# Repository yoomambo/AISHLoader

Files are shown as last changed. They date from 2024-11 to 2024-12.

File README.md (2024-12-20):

# Installation
First, download the application and install dependencies:
```bash
git clone https://github.com/BenjaminLam9838/AISHLoader
cd AISHLoader
```

Create a virtual environment and install the dependencies.  This app was built on Python 3.9.13 ([pyFirmata has issues in 3.11 [1]](#1-pyfirmata-has-issues-in-311))
```bash
python3.9 -m venv .venv
source .venv/bin/activate
pip install --upgrade pip
pip install -r requirements.txt
```
# To do:
Hardware:
- [ ] Adjust linear rail alignment. Currently, it is slightly misaligned with the alignment rails and does not insert perfectly
- [ ] Increase stiffness of the gripper if the gripping is not consistent.

Software:
- [ ] Test abortion feature.  Currently, the abortion procedure is not quite complete
- [ ] Known bug: pausing the queue when an experiment is running will make the queue pause after the current experiment is done (will not send the next experiment after finish).  But pressing resume before the experiment is done just sends the next experiment, even if the current one is not finished, causing an error. Likely fix: change logic to just toggle the queue pause state, and remove sendNextItem() function in the resume button callback.
- [ ] Test data saving location for XRD data

# Control Interface Guide


The web UI is broken into 4 main parts:
- Add to queue (Blue) - adds items to the queue with all the experimental parameters.
- Queue (Green) - displays queued items and updates when items are executed. The items can be dragged to reorder.
- System status (Red) - displays the current system state.
- Manual control (Orange) - collapsable menu that contains buttons to manually control all components of the AISH Loader.

# System Diagram
## Top-level Flowchart

The python/Flask server controls the entire system. It recieves HTTP requests to the API endpoints either from the website (user input), or from ALab; these HTTP requests are intended to work for both cases and be the minimum set of instructions needed to control the system.

The Flask server then communicates over pyFirmata (based on serial) with the Arduino to control the gripper and linear rail, and directly communicates with the Ender3 over serial.  This server runs on the XRD computer and writes to a local directory to control the XRD.

## Wiring Diagram:


# CAD
A Solidworks CAD is supplied in the /cad.  A full BOM is left in /documentation.

# Stepper Motor Driver
A `STEPPERONLINE Stepper Motor Driver` controller was used to control the linear rail. It was set to 400 pulses/rotation, meaning that each time the Arduino pulses the motor driver, the motor rotates 1/400 of a rotation.  The pinout used is shown below:



Errors
===
### Manual adjustment of Ender3
Sometimes, manual adjustment of the Ender3 needs to be done to put it in a position that is good for testing.  The gantry cannot be manipulated when the Ender is powered, so it must be de-powered.  Remember to unplug the Serial connection, then power down the Ender.  Follow the procedure in [Ender3 Connection](#Ender3-Connection).

### Ender3 Connection
When the Ender3 is not connected properly, the unit scale gets changed.  This usually results in the Ender moving about 1/2 the distance that is inputted.  To fix, restart the system, unplug the serial connection to the Ender, and power cycle the Ender.  Make sure to wait for the Ender to start up and be ready, then plug in the serial connection and try the connection.

### Connecting Serial
The system has trouble connecting at first.  Unplug the serial connections, then unpower/repower the extender cables, then reconnect the serial connections.  Basically have to power/unpower the first connector, then connect the next connector, unpower and power that, then can continue connecting.

Notes
===
#### [1] pyFirmata has issues in 3.11
[pyFirmata's Github](https://github.com/tino/pyFirmata/tree/master) says it runs on python 3.7.

When calling ```board = pyfirmata.Arduino('/dev/tty.usbmodem21101')```, an AttributeError is thrown: ```AttributeError: module 'inspect' has no attribute 'getargspec'. Did you mean: 'getargs'?```.
ChatGPT says:
> The error you're encountering is due to the use of the inspect.getargspec method in pyfirmata, which has been deprecated and removed in Python 3.11. Instead, inspect.getfullargspec should be used.

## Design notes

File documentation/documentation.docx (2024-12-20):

# Hardware

## app.py

Sets up the Flask server by defining all the endpoints. The endpoints are organized into API Endpoints, which are the endpoints intended for use, and manual endpoints, which give direct manual control over the available system actions.

On start, the application attempts a connection to the 3D printer over serial and performs its homing procedure. It then attempts a connection to the Arduino over serial/pyFirmata and homes its components. If either of these connections fail, the server will not start, unless WEBSITE_TEST_MODE is on.

The connections to the Ender and Arduino are made by a AISHLoader object, which contains all the relevant functions and actions for the loading/unloading procedures. A AISHExperiment object is created when the system is given an experiment and this class contains all the relevant functions and actions to execute an XRD experiment. The aish_experiment variable is set to null if there is no currently running experiment.

## AISHExperiment.py

Contains the relevant functions and actions to execute an XRD experiment. The Diffractometer class is taken from Nathan’s AdaptiveXRD code (https://github.com/njszym/AdaptiveXRD) to run the Bruker. The run_sequence function is a blocking function that runs all XRD scans at the given temperatures. Since it is blocking, the Flask server runs this function in a separate thread to prevent the server from stalling when an experiment runs.

## AISHLoader.py

Contains relevant functions and actions for the loading/unloading procedures. This is meant to be an abstraction layer to help group the low level procedures together.

## ArduinoHardware.py

Contains the control code for the Gripper and Linear rail, which are each subclasses. Each command is assigned a unique Firmata sysex command ID, which instructs the Arduino to execute its various actions. It then listens for an acknowledgement from the Arduino that the command was completed (blocking).

## Ender3.py

Contains the control code for the Ender3. This class writes gcode commands to the serial bus to control movement. Most of the movements utilize _move_to(x,y,z, speed) which is a function that sends the required gcode to move to the specified x,y,z position. This function is also blocking, so each move will be completed before moving to the next.

## AISH_utils.py

Contains classes to handle communication timeouts that may occur. Since the system runs in semi open-loop, some actions are not verified completed. So these functions allow the system to ask the user to confirm that an action was completed.

## StateTracker.py

Helper class that logs the last 100 states. The other hardware classes inherit from this class, so all of them have a list of the last 100 states they were in. These states are just strings. Meant for debugging but could be helpful for logs.

# Website

## templates > index.html

Contains the html for the web UI to queue experiments. Also includes the UI for manual control of all system components

## static > js > app.js

app.js contains all the js components for website communication with the Flask server, and updating components on the webpage.

The webpage first loads utils.js, then loads app.js. app.js attaches all button callbacks when the website has loaded. A loop is started to refresh the webpage state every set interval where the webpage asks the Flask server for the current system state and displays that to the webpage.

## static > js > utils.js

utils.js includes tools for rendering the webpage like experiment time estimation, dynamic button layout (the buttons for the sample positions are generated with js).

# Arduino Code

## AISHLoader

Essentially a switch-case list of the different commands that the Arduino will perform.

## Tests > LinearRail_Testing

Tests the Linear rail motion. Takes input from the serial monitor for how many steps to move (+ for up, - for down) and “home” to execute the homing procedure. Use this to dial in the amount of throw for the linear rail.

## Tests > Servo_SerialTesting

Tests the gripper servo motion. Takes input from the serial monitor of the angle to move the servo to.

# Calibration

The sample positions of the Ender sometimes has to be recalibrated. The positions are found by finding the 4 corner positions, and the rest are interpolated. The calibration script moves the gripper to the desired position, moves down to grab the sample, lifts it, then puts it back. The sample should not scrape against the holder. My testing seems to show that there +/- 0.3 mm of tolerance from perfectly centered.

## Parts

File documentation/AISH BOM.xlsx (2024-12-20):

Assembly | Part | Quantity | Link | Comments | Price
InSituXRD_ASSM > StageLoader_ASSM | FuyuRail_ASSM | 1 | https://www.amazon.com/FUYU-Actuator-Motorized-Stepper-Sliders/dp/B0CRKGDDY6?ref_=ast_sto_dp&th=1 |  | 84.15
InSituXRD_ASSM > StageLoader_ASSM > RailFrame_ASSM | 47065T411 | 2 | https://www.mcmaster.com/47065T101-47065T553/ | T-Slotted Framing 12" | 8.67
InSituXRD_ASSM > StageLoader_ASSM > RailFrame_ASSM | 47065T553 | 3 | https://www.mcmaster.com/47065T101-47065T553/ | T-Slotted Framing 6" | 6.06
InSituXRD_ASSM > StageLoader_ASSM > RailFrame_ASSM | 47065T239 | 2 | https://www.mcmaster.com/47065T239/ |  | 8
InSituXRD_ASSM > StageLoader_ASSM > RailFrame_ASSM | 47065T663_Silver Gusset Bracket | 5 | https://www.mcmaster.com/47065T663/ |  | 9.97
InSituXRD_ASSM > StageLoader_ASSM > StageMount_Multipart_ASSM | 5537T658_T-Slotted Framing | 2 | https://www.mcmaster.com/5537T658/ | Stage mount bracket | 10.54
InSituXRD_ASSM > StageLoader_ASSM > StageMount_Multipart_ASSM | StageMount_Multipart_ MountPlate | 1 |  | 3D print
InSituXRD_ASSM > StageLoader_ASSM > StageMount_Multipart_ASSM | StageMount_Multipart_ TopPlate | 1 |  | 3D print NYLON
InSituXRD_ASSM | 91290A332 | 4 | https://www.mcmaster.com/91290A332/ | Bolts for Stage | 0.222
InSituXRD_ASSM | 9657K275 | 4 | https://www.mcmaster.com/9657K275/ | Springs for stage | 0.965
InSituXRD_ASSM > SampleLoader_ASSM | 01 MAIN ASM Ender_3 | 1
InSituXRD_ASSM > SampleLoader_ASSM | SampleLoader_SampleBufferPlate | 1 |  | 3D print
InSituXRD_ASSM > SampleLoader_ASSM > Gripper_ASSM | DS3218MG MS24 Digital Servo 270 | 1
InSituXRD_ASSM > SampleLoader_ASSM > Gripper_ASSM | Gripper_ServoCouplin g | 1 |  | 3D print
InSituXRD_ASSM > SampleLoader_ASSM > Gripper_ASSM | Gripper_ServoMount_V 2 | 1 |  | 3D print
InSituXRD_ASSM > SampleLoader_ASSM > Gripper_ASSM | Gripper_Claw_OffsetL_ v2 | 1 |  | 3D print
InSituXRD_ASSM > SampleLoader_ASSM > Gripper_ASSM | Gripper_Claw_OffsetR_ v2 | 1 |  | 3D print
InSituXRD_ASSM > SampleLoader_ASSM > Gripper_ASSM | 91290A117 | 2 | https://www.mcmaster.com/91290A117/ | bolts for gripper arms | 0.1129

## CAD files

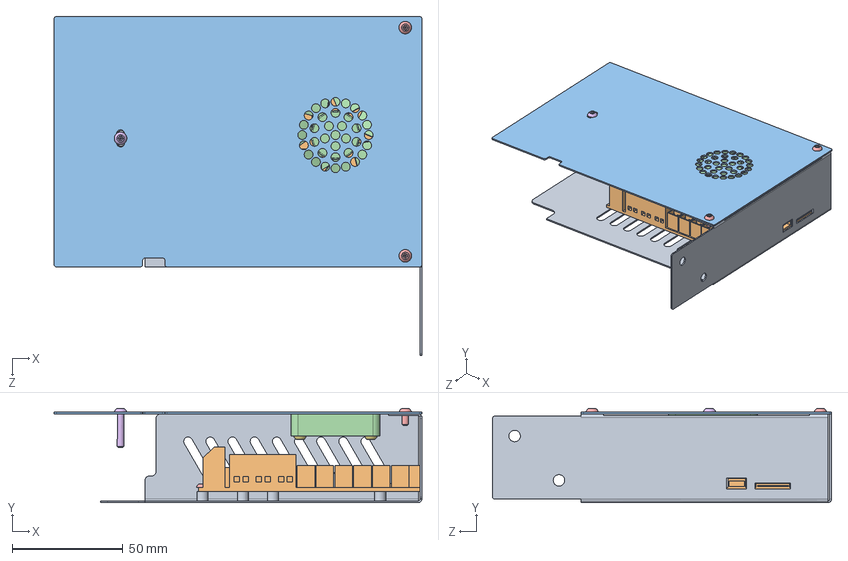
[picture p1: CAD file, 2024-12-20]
cad/SampleLoader/Ender-3/ASM Electronic Enclosure.SLDASM
166.0 x 42.5 x 153.0 mm
Sheetmetal enclosure bottom
Control panel
Sheetmetal enclosure top
Case fan
M3X6Pan Head Screw x 6
M3X16 Pan Head Screw
M3X10 Pan Head Screw x 2

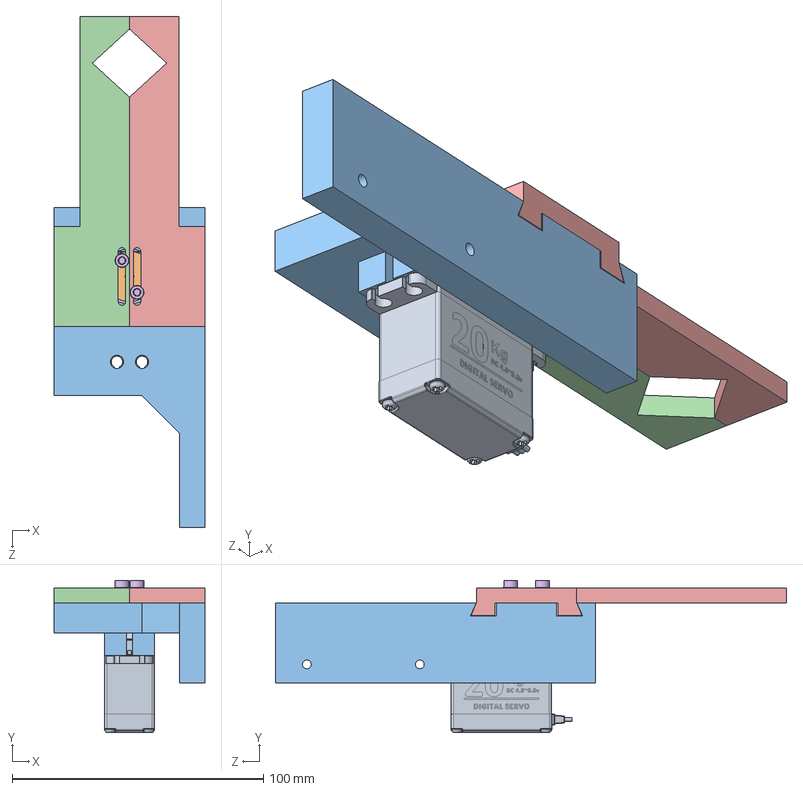
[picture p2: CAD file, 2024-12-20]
cad/SampleLoader/Gripper/Gripper_ASSM_v2.SLDASM
60.0 x 60.7 x 203.6 mm
DS3218MG MS24 Digital Servo 270
Gripper_ServoCoupling
Gripper_ServoMount_V2
Gripper_Claw_OffsetL_v2
Gripper_Claw_OffsetR_v2
91290A117_Alloy Steel Socket Head Screw x 2

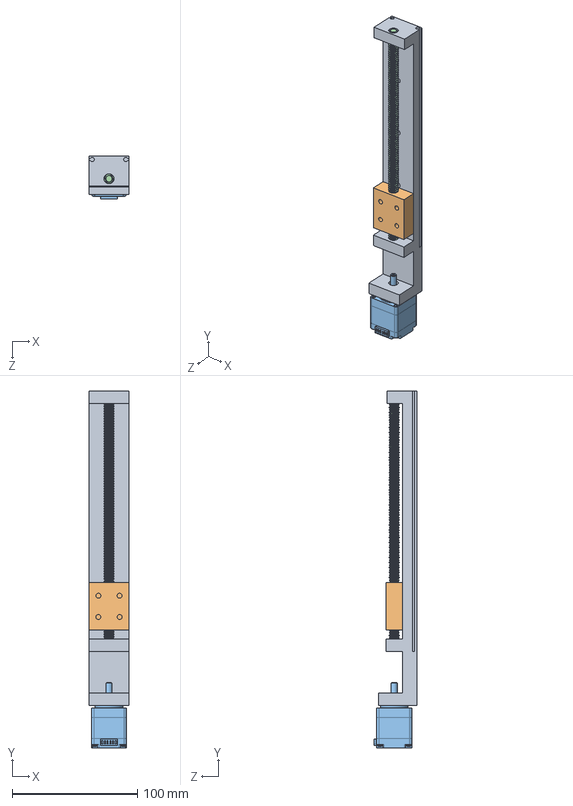
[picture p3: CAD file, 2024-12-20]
cad/StageLoader/FuyuRail/FuyuRail_ASSM.SLDASM
32.0 x 285.0 x 34.0 mm
FuyuRail_Body
FuyuRail_Coupling
6627T37_Stepper Motor
97783A170_Fast-Travel Ultra-Precision Lead Screw

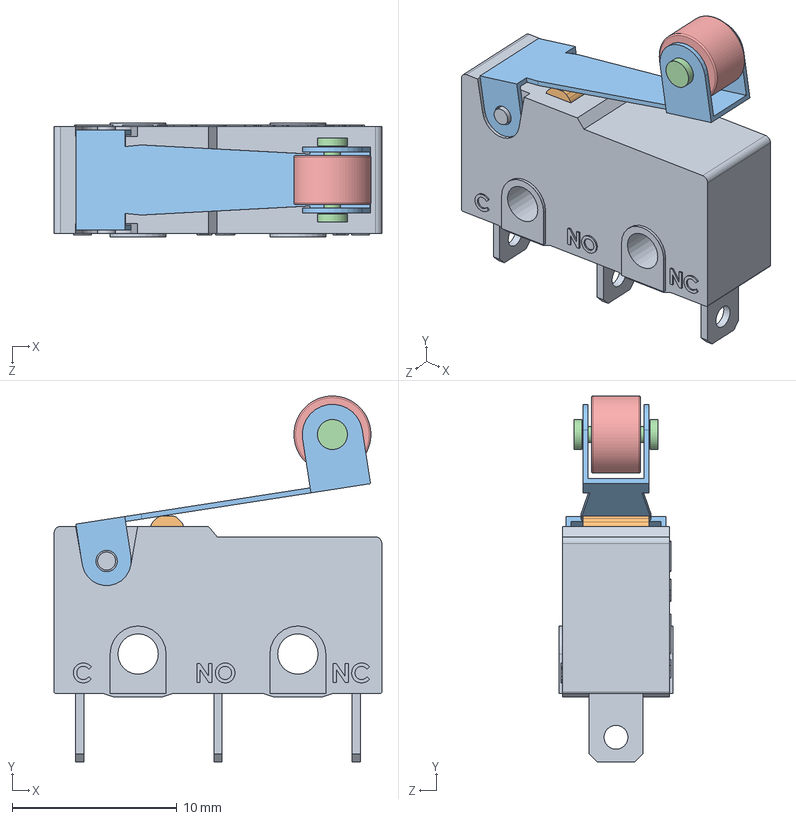
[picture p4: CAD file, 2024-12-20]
cad/StageLoader/limit-switch-19.snapshot.1/Limit Switch.SLDASM
19.9 x 22.2 x 6.90 mm
Switch_Button
Link
Wheel shaft
Wheel

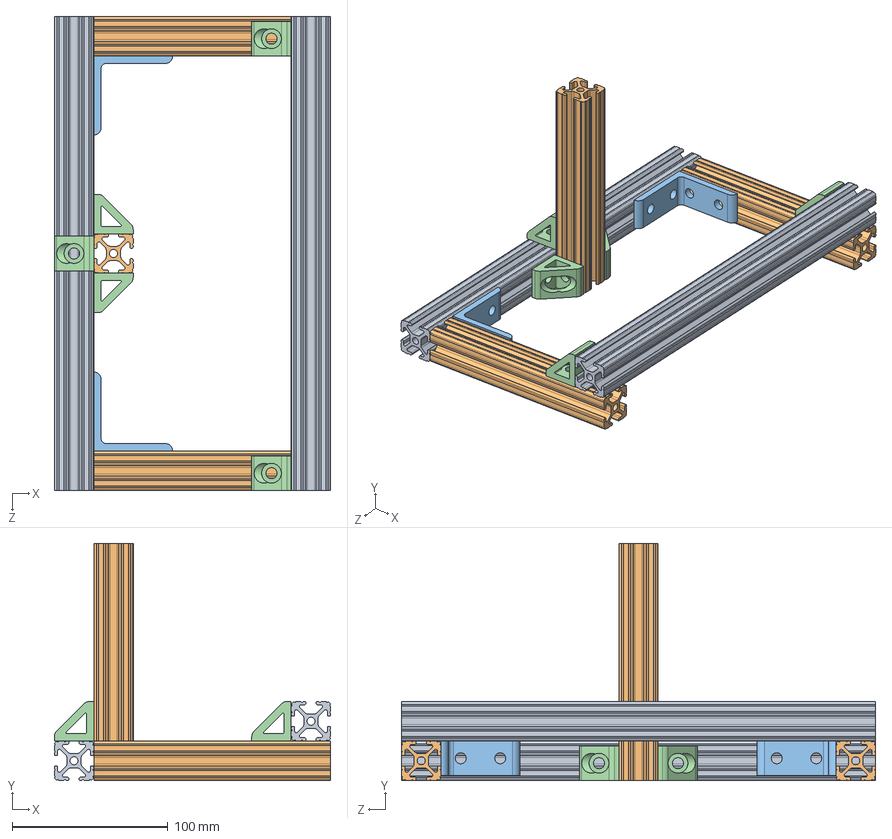
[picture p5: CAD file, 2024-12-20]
cad/StageLoader/RailFrame/RailFrame_ASSM.SLDASM
177.8 x 152.4 x 304.8 mm
47065T411_T-Slotted Framing x 2
47065T553_T-Slotted Framing x 3
47065T239_Silver Corner Bracket x 2
47065T663_Silver Gusset Bracket x 5

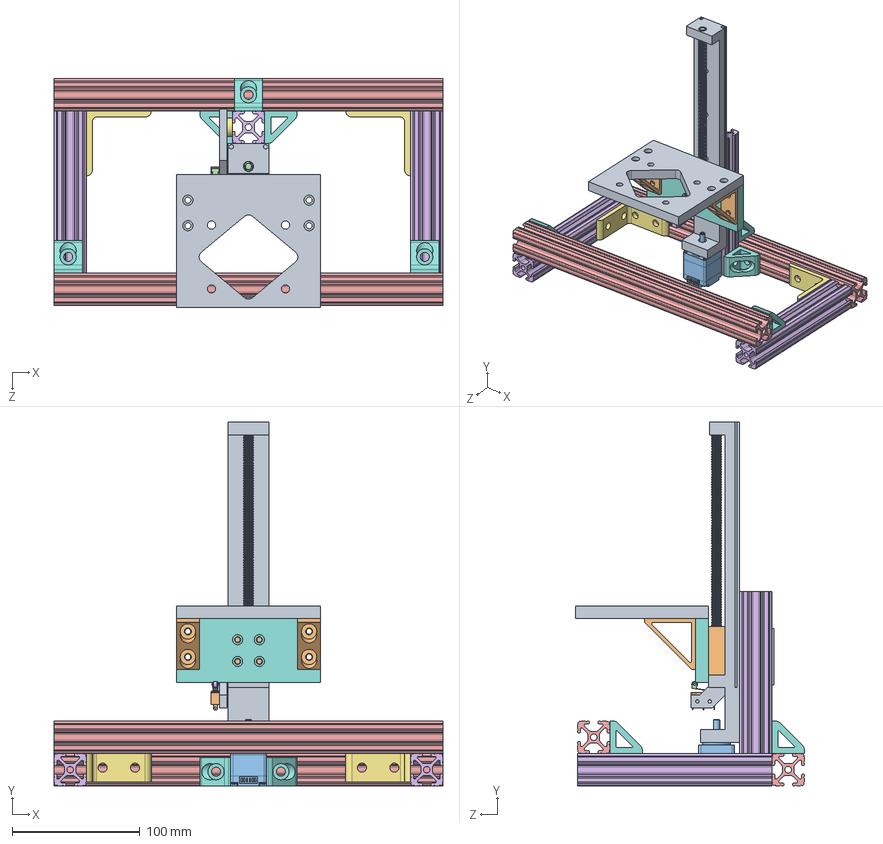
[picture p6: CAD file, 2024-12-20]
cad/StageLoader/StageLoader_ASSM.SLDASM
304.8 x 285.0 x 179.3 mm
FuyuRail_Body
FuyuRail_Coupling
6627T37_Stepper Motor
97783A170_Fast-Travel Ultra-Precision Lead Screw
47065T411_T-Slotted Framing x 2
47065T553_T-Slotted Framing x 3
47065T239_Silver Corner Bracket x 2
47065T663_Silver Gusset Bracket x 5
StageLoader_LimitSwitchTslot2
Switch_Button
Link
Wheel shaft
Wheel
StageLoader_LimitSwitchTslot2_spacer
StageMount_Multipart_MountPlate
StageMount_Multipart_TopPlate
5537T658_T-Slotted Framing x 2

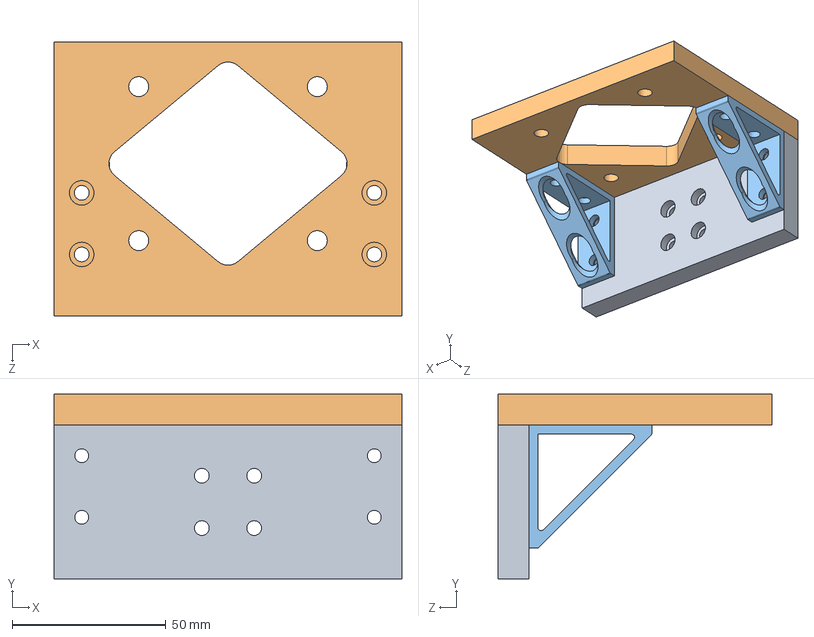
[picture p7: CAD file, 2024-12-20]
cad/StageLoader/StageMount_Multipart/StageMount_Multipart_ASSM.SLDASM
113.0 x 60.0 x 89.0 mm
StageMount_Multipart_MountPlate
StageMount_Multipart_TopPlate
5537T658_T-Slotted Framing x 2

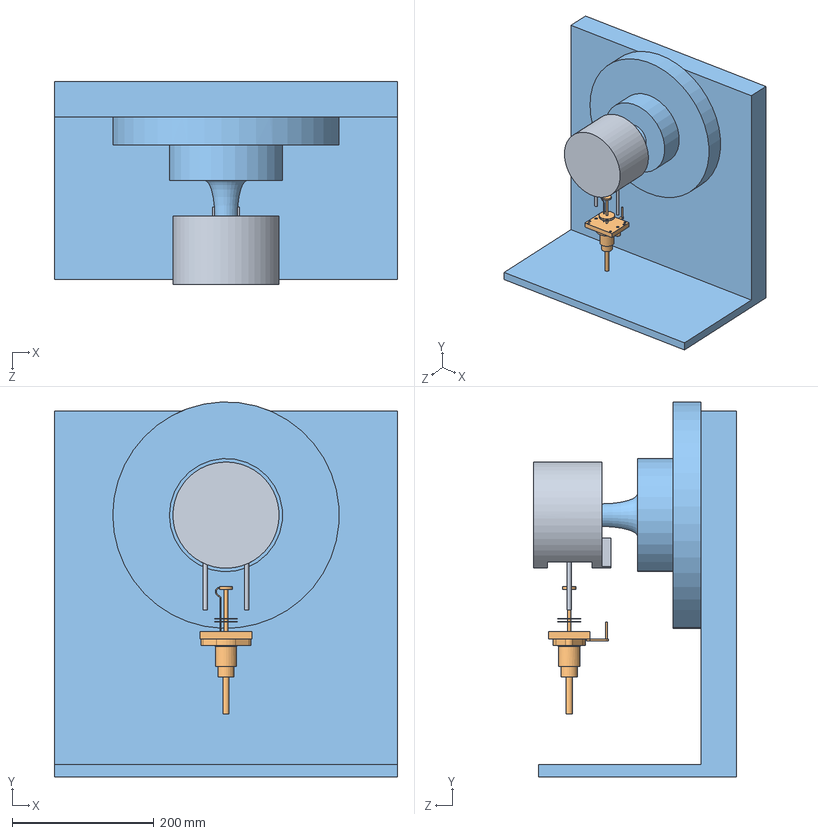
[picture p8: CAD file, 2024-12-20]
cad/XRD/XRD_ASSM.SLDASM
485.0 x 530.0 x 287.0 mm
XRD_FurnaceBody
XRD_SampleStage
XRD_Frame

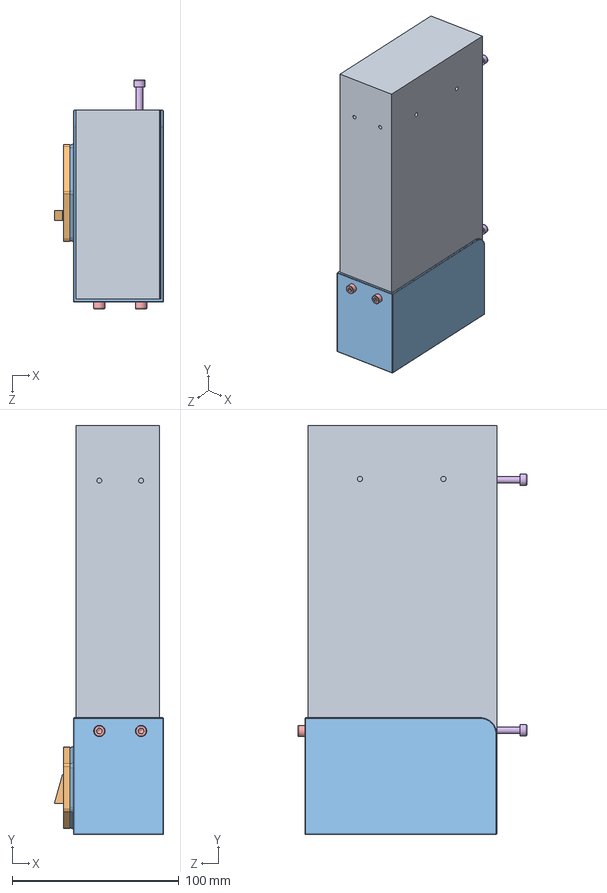
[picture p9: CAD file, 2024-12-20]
cad/SampleLoader/Ender-3/ASM Power Supply.SLDASM
65.5 x 245.0 x 137.0 mm
24V15A power supply
power switch
Power holder
M3X10 Flush Head Screw x 2
M4X8 Socket Head Screw x 2
M4X20 Socket Head Screw x 2

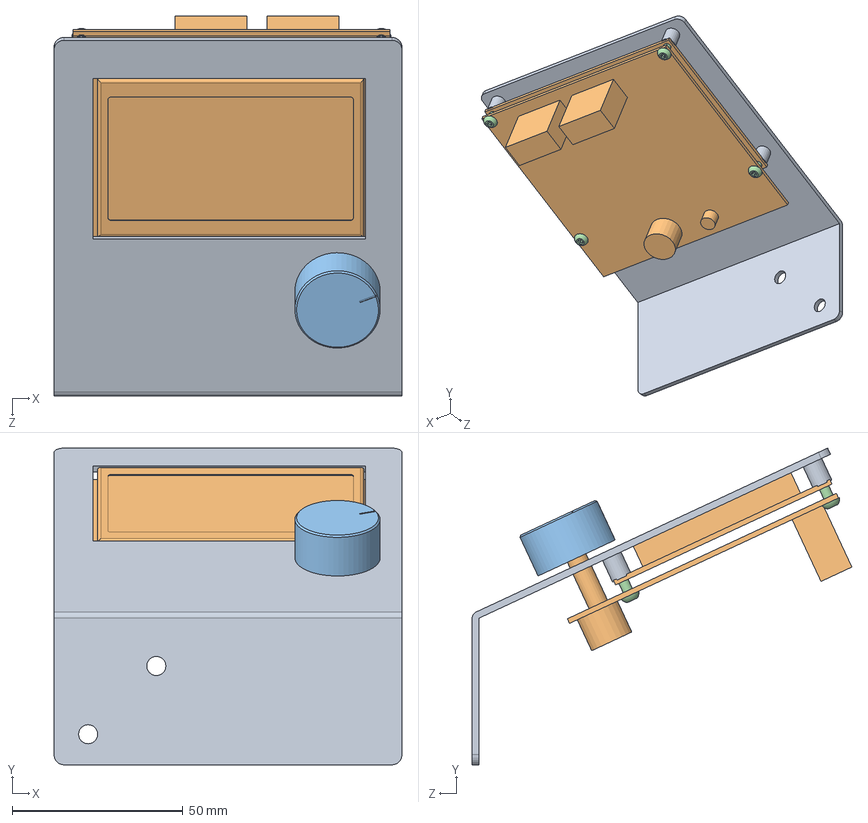
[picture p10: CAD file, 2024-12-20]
cad/SampleLoader/Ender-3/ASM Display.SLDASM
102.0 x 92.9 x 111.3 mm
LCD support
lcd
lcd Knob
M3X8 Pan Head Screw x 4

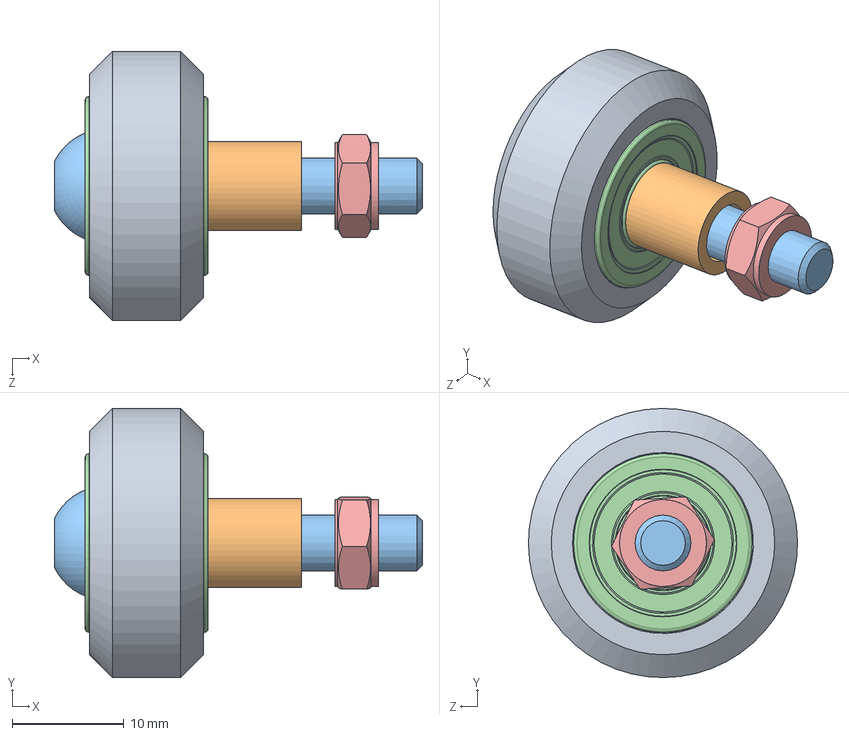
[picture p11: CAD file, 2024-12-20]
cad/SampleLoader/Ender-3/ASM Roller Z-Axis Right.SLDASM
33.0 x 24.1 x 24.1 mm
Rollers
Spacers for rollers
M5X30 Pan Head Screw
625pillow x 2
M5 Self-locking nut

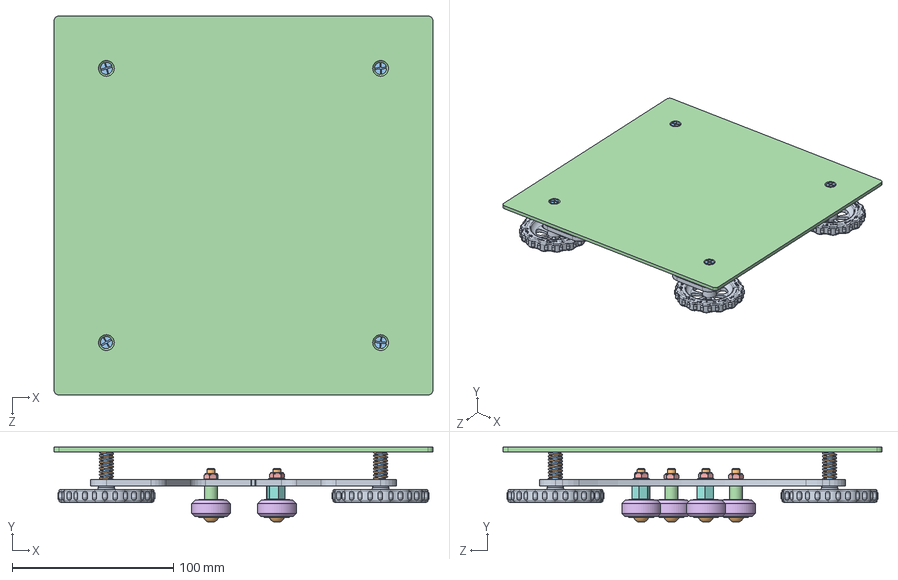
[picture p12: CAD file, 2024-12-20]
cad/SampleLoader/Ender-3/ASM Bed.SLDASM
235.0 x 46.2 x 235.0 mm
Y plate
M5X30 Pan Head Screw x 4
625pillow x 8
Spacers for rollers x 2
M5 Self-locking nut x 4
Rollers x 4
M5 washer x 2
Eccentric column x 2
Hand Twisted Nut x 4
Bed level springs x 4
M4X30 Flush Head Screw x 4
Hot bed

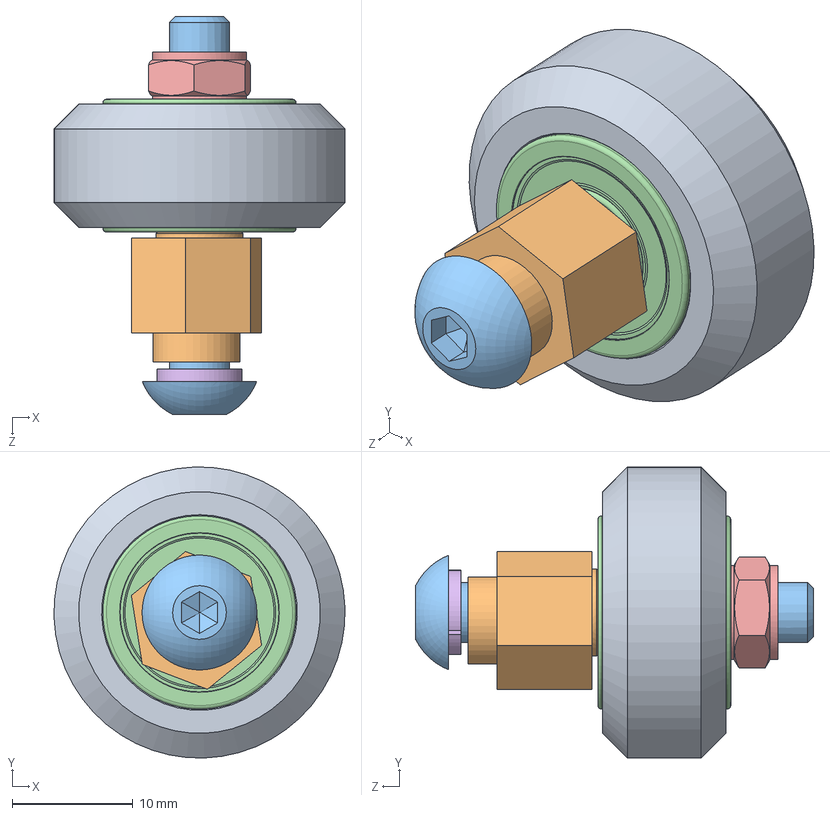
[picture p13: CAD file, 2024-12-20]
cad/SampleLoader/Ender-3/ASM Eccentrical Roller Z-Axis Right.SLDASM
24.1 x 24.1 x 33.0 mm
Rollers
Eccentric column
M5X30 Pan Head Screw
625pillow x 2
M5 Self-locking nut
M5 Split Washer

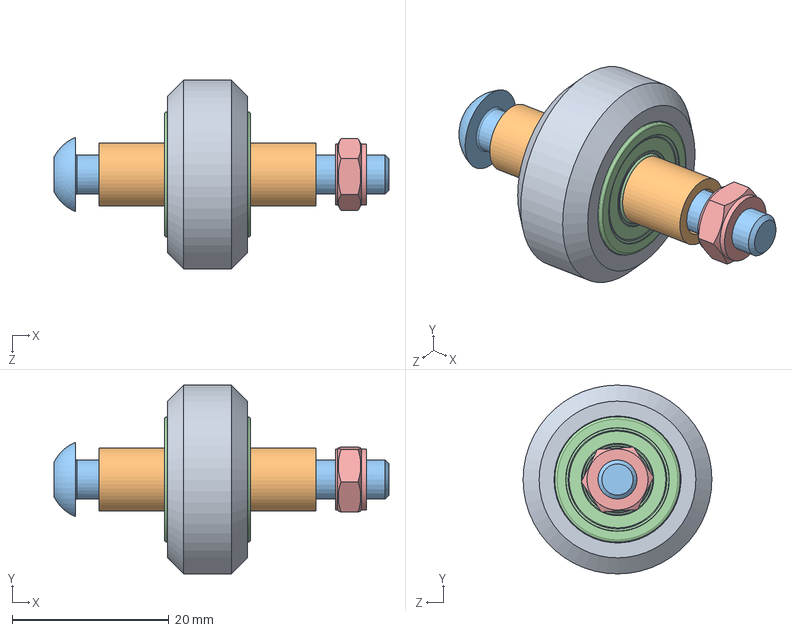
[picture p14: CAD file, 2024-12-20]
cad/SampleLoader/Ender-3/ASM Roller Z-Axis Left.SLDASM
42.8 x 24.1 x 24.1 mm
Rollers
Spacers for rollers x 2
M5X40 Pan Head Screw
625pillow x 2
M5 Self-locking nut

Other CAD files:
cad/SampleLoader/Ender-3/ASM Roller Y-Axis.SLDASM
cad/SampleLoader/Ender-3/ASM Y-Belt Tensioner.SLDASM
cad/SampleLoader/Ender-3/ASM Eccentrical Roller Z-Axis Left.SLDASM
cad/SampleLoader/Ender-3/ASM X-Belt Tensioner.SLDASM
cad/1272T361_Multipurpose 304 Stainless Steel Rod.SLDPRT
cad/91290A332_Alloy Steel Socket Head Screw.SLDPRT
cad/9657K275_Compression Spring.SLDPRT
cad/InsituXRD_AlignmentBracket.SLDPRT
cad/InsituXRD_ControlBox.SLDPRT
cad/InsituXRD_RodHolder.SLDPRT
cad/SampleLoader/Ender-3/2020 Endcap.SLDPRT
cad/SampleLoader/Ender-3/2020 profile.SLDPRT
cad/SampleLoader/Ender-3/2020-2 profile.SLDPRT
cad/SampleLoader/Ender-3/2040-2 profile.SLDPRT
cad/SampleLoader/Ender-3/2040-3L profile.SLDPRT
cad/SampleLoader/Ender-3/2040-3R profile.SLDPRT
cad/SampleLoader/Ender-3/24V15A power supply.SLDPRT
cad/SampleLoader/Ender-3/2GT-pulley.SLDPRT
cad/SampleLoader/Ender-3/4040 profile.SLDPRT
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

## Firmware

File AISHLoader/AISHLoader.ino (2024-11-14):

#include <Boards.h>
#include <Firmata.h>
#include <FirmataConstants.h>
#include <FirmataDefines.h>
#include <FirmataMarshaller.h>
#include <FirmataParser.h>

#include <Servo.h>

Servo gripperServo;  // create Servo object to control a servo
#define SERVO_SPEED_DELAY 15
#define servoPin 9


// Define stepper motor connection pins
#define RAIL_limPin 5   //Limit switch
#define RAIL_dirPin 6   // Direction pin
#define RAIL_stepPin 7  // Step pin
#define RAIL_enPin 8    //Enable pin

// Define the number of steps per revolution for motor
#define RAIL_STEPS_PER_REV 400
#define RAIL_PULSEWIDTH 300  // Controls the speed, longer = slower
int RAIL_stepCount = -1;     // Tracks the current number of steps of the stepper motor rail.  75*400 = 30 000, which is storable in signed int

void setup() {
  Firmata.setFirmwareVersion(FIRMATA_FIRMWARE_MAJOR_VERSION, FIRMATA_FIRMWARE_MINOR_VERSION);
  Firmata.begin(57600);

  // Attach SysEx callback handler
  for (uint8_t i = 0; i < 0x50; i++)
    Firmata.attach(i, sysexCallback);

  //Initialize servo to 0 (open)
  gripperServo.attach(servoPin);  // attaches the servo to the Servo object
  moveServo(0);

  //Initialize the input/output pins for the linear rail
  pinMode(RAIL_stepPin, OUTPUT);
  pinMode(RAIL_dirPin, OUTPUT);
  pinMode(RAIL_enPin, OUTPUT);
  pinMode(RAIL_limPin, INPUT_PULLUP);  //Normally open

  digitalWrite(RAIL_enPin, LOW);    //Turn off current through the motor
  digitalWrite(RAIL_stepPin, LOW);  //Initialize the pulsing pin to low
  digitalWrite(RAIL_dirPin, HIGH);  //Set direction to up
}

void loop() {
  // Handle any incoming Firmata messages
  while (Firmata.available()) {
    Firmata.processInput();
  }
}

void sysexCallback(byte command, byte argc, byte* argv) {
  // Echo back the received SysEx message
  switch (command) {
    //LINEAR RAIL CALLBACKS
    case 0x20:  //Linear rail go up
      {
        rotateMotor(10 * RAIL_STEPS_PER_REV);
        byte data = 0xFF;
        Firmata.sendSysex(command, 1, &data);  //Send a 0xFF byte to indicate it is finished and successful
        break;
      }
    case 0x21:  //Linear rail go down
      {
        rotateMotor(-10 * RAIL_STEPS_PER_REV);
        byte data = 0xFF;
        Firmata.sendSysex(command, 1, &data);  //Send a 0xFF byte to indicate it is finished and successful
        break;
      }
    case 0x22:  //Get the stepper motor count of the linear rail
      {
        byte data[2];

        // Break the int into 2 bytes
        data[0] = (RAIL_stepCount >> 8) & 0xFF;
        data[1] = RAIL_stepCount & 0xFF;

        // Send the data as a Sysex message
        Firmata.sendSysex(command, 2, data);  // 0x71 is an example command ID
        break;
      }
    case 0x23:  //Home the rail
      {
        bool homeSuccess = homeRail();
        if (homeSuccess) {
          byte data = 0xFF;
          Firmata.sendSysex(command, 1, &data);  //Send a 0xFF byte to indicate it is finished and successful
        } else {
          byte data = 0x00;
          Firmata.sendSysex(command, 1, &data);  //Send a 0xFF byte to indicate it is finished and successful
        }
        break;
      }


    //GRIPPER CALLBACKS
    //Gripper grabbing commands
    case 0x10:  //Open Gripper
      {
        gripper_grab(false);
        byte data = 0xFF;
        Firmata.sendSysex(command, 1, &data);  //Send a 0xFF byte to indicate it is finished and successful
        break;
      }
    case 0x11:  //Close Gripper
      {
        gripper_grab(true);
        byte data = 0xFF;
        Firmata.sendSysex(command, 1, &data);  //Send a 0xFF byte to indicate it is finished and successful
        break;
      }
    // Check the state of the gripper
    case 0x12:  //Get gripper state (Open/closed)
      {
        byte value_to_send = (gripperServo.read() == 30) ? 1 : 0;  // Convert boolean to integer
        Firmata.sendSysex(command, 1, &value_to_send);             // Send the integer value
        break;
      }
    case 0x14:  //Get gripper servo angle
      {
        byte value_to_send = byte(gripperServo.read());
        Firmata.sendSysex(command, 1, &value_to_send);  // Send the integer value
        break;
      }

    //Test, echo back the command
    case 0x01:
      {
        Firmata.sendSysex(command, argc, argv);
        break;
      }
    //Test, send back 4 bytes of data [23, 14, 22, 14]
    case 0x02:
      {
        byte data[4];
        data[0] = 23;
        data[1] = 14;
        data[2] = 22;
        data[3] = 14;

        Firmata.sendSysex(command, 4, data);
        break;
      }
  }
}


/**
 * @brief Performs the homing procedure for the rail by moving towards a limit switch.
 *
 * This function first checks if the limit switch is already pressed. If pressed, it rotates the motor 
 * upwards by 4 full revolutions to disengage the switch. Then, the motor moves towards the limit switch 
 * until either the limit switch is triggered (indicating successful homing) or a maximum step count is 
 * reached (indicating timeout).  Ths maximum is half of the total throw of the linear rail (75/2 rotations)
 *
 * @return bool - Returns true if homing is successful (limit switch triggered), otherwise false (timeout).
 */
bool homeRail() {
  long maxSteps = (20 * RAIL_STEPS_PER_REV);  // Timeout condition
  long stepsMoved = 0;

  // Serial.print("Max Steps (homing): ");
  // Serial.println(maxSteps);

  // (1) Check if the limit switch is already pressed.  If so, translate upwards by a little bit
  if (digitalRead(RAIL_limPin) == LOW) {  // Limit switch is already pressed
    rotateMotor(4 * RAIL_STEPS_PER_REV);
  }

  // (2) Do homing procedure
  // Serial.println("Starting homing");
  digitalWrite(RAIL_dirPin, LOW);                                      // Set direction towards the limit switch
  digitalWrite(RAIL_enPin, HIGH);                                      // Enable motor
  while (digitalRead(RAIL_limPin) == HIGH && stepsMoved < maxSteps) {  // Move until the limit switch is pressed or timeout
    digitalWrite(RAIL_stepPin, LOW);
    delayMicroseconds(RAIL_PULSEWIDTH);  // Adjust this delay to control speed
    digitalWrite(RAIL_stepPin, HIGH);
    delayMicroseconds(RAIL_PULSEWIDTH);
    stepsMoved++;
    RAIL_stepCount--;
  }

  digitalWrite(RAIL_enPin, LOW);  // Disable motor once homed or timeout (no locking)

  // Serial.println(stepsMoved);
  if (stepsMoved >= maxSteps) {
    // Serial.println("Homing failed: Timeout reached");
    return false;
  } else {
    RAIL_stepCount = 0;  // Reset the step count after successful homing
    // Serial.print("Homing successful.");
    // Serial.print("  Steps Moved: ");
    // Serial.println(stepsMoved);
    return true;
  }
}



/**
 * Rotates the stepper motor a specified number of revolutions.
 *
 * This function controls the direction and steps of a stepper motor based on the input
 * revolutions. Positive values will rotate the motor clockwise, while negative values will
 * rotate it counter-clockwise. The motor is enabled before rotation and disabled afterward.
 *
 * @param pulseCount  The number of pulses to send to the motor. Rotates pulseCount*RAIL_STEPS_PER_REV revolutions
 *                    Use a positive float for clockwise rotation and a negative 
 *                    float for counter-clockwise rotation.
 */
void rotateMotor(long pulseCount) {
  if (abs(pulseCount) > 75 * RAIL_STEPS_PER_REV)
    return;

  digitalWrite(RAIL_enPin, HIGH);
  delay(500);

  int dir = 1;
  // Determine direction and total steps
  if (pulseCount > 0) {
    digitalWrite(RAIL_dirPin, HIGH);  // Clockwise
    dir = 1;
  } else {
    digitalWrite(RAIL_dirPin, LOW);  // Counter-clockwise
    dir = -1;
  }

  int totalSteps = abs(pulseCount);

  for (int x = 0; x < totalSteps; x++) {
    digitalWrite(RAIL_stepPin, LOW);
    delayMicroseconds(RAIL_PULSEWIDTH);  // Adjust this delay to control speed
    digitalWrite(RAIL_stepPin, HIGH);
    delayMicroseconds(RAIL_PULSEWIDTH);

    RAIL_stepCount += dir;  //Keep a running count of the steps
  }

  digitalWrite(RAIL_enPin, LOW);  //Cut current to motor (no locking)
}




/**
 * Controls the gripper's grab action by setting the servo position.
 *
 * This function activates or deactivates the gripper based on the `isGrabOn` parameter.
 * When `isGrabOn` is true, the servo moves to the "grab" position (30 degrees).
 * When `isGrabOn` is false, the servo moves to the "release" position (0 degrees).
 *
 * @param isGrabOn A boolean value where true activates the grab action, 
 *                 and false releases the gripper.
 */
void gripper_grab(bool isGrabOn) {
  if (isGrabOn) {
    moveServo(45);
  } else {
    moveServo(0);
  }
}
/**
 * Moves the servo to the specified target position at the given speed.
 *
 * This function gradually moves the servo from its current position to the target 
 * position by incrementing or decrementing in 1-degree steps. The speed of movement 
 * is controlled by the delay between each step.
 *
 * @param targetPos The target position to move the servo to (0 to 180 degrees).
 * @param speed The speed of movement, where a higher value results in slower movement. 
 *              This is the delay in milliseconds between each degree step.
 */
void moveServo(int targetPos) {
  int currentPos = gripperServo.read();  // get the current position of the servo
  if (targetPos >= 0 && targetPos <= 180) {
    if (currentPos < targetPos) {
      for (int pos = currentPos; pos <= targetPos; pos++) {
        gripperServo.write(pos);   // move the servo to the next position
        delay(SERVO_SPEED_DELAY);  // control the speed
      }
    } else {
      for (int pos = currentPos; pos >= targetPos; pos--) {
        gripperServo.write(pos);   // move the servo to the next position
        delay(SERVO_SPEED_DELAY);  // control the speed
      }
    }
  }
}

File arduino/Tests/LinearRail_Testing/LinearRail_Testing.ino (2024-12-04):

//FUYU RAIL IS 75 REVOLUTIONS END TO END (Leaves a small gap)

// Define Stepper motor limit switch
#define limPin 5

// Define stepper motor connection pins
#define dirPin 6   // Direction pin
#define stepPin 7  // Step pin
#define enPin 8

// Define the number of steps per revolution for your motor
#define STEPS_PER_REV 400
#define PULSEWIDTH 300  // Controls the speed, longer = slower
long stepCount = -1;

void setup() {
  // Declare pins as outputs
  pinMode(stepPin, OUTPUT);
  pinMode(dirPin, OUTPUT);
  pinMode(enPin, OUTPUT);
  pinMode(limPin, INPUT_PULLUP);  //Normally open

  Serial.begin(9600);  // Initialize serial communication
  digitalWrite(enPin, LOW);
  digitalWrite(stepPin, LOW);
  digitalWrite(dirPin, HIGH);

  delay(1000);
}

void loop() {
  // Serial.println(digitalRead(limPin));
  if (Serial.available() > 0) {
    String input = Serial.readStringUntil('\n');  // Read the input as a string

    if (input.equals("home")) {
      homeRail();  // Call homeRail() if "home" is input
    } else {
      int revolutions = input.toInt();  // Convert input to an integer
      rotateMotor(revolutions);         // Rotate based on the input value
    }

    delay(1000);  // Wait for 2 seconds after each operation
    Serial.println(stepCount);
  }
}

/**
 * @brief Performs the homing procedure for the rail by moving towards a limit switch.
 *
 * This function first checks if the limit switch is already pressed. If pressed, it rotates the motor 
 * upwards by 4 full revolutions to disengage the switch. Then, the motor moves towards the limit switch 
 * until either the limit switch is triggered (indicating successful homing) or a maximum step count is 
 * reached (indicating timeout).
 *
 * @return bool - Returns true if homing is successful (limit switch triggered), otherwise false (timeout).
 */
bool homeRail() {
  long maxSteps = (75 * STEPS_PER_REV / 2);  // Timeout condition
  long stepsMoved = 0;

  // Serial.print("Max Steps (homing): ");
  // Serial.println(maxSteps);

  // (1) Check if the limit switch is already pressed.  If so, translate upwards by a little bit
  if (digitalRead(limPin) == LOW) {  // Limit switch is already pressed
    rotateMotor(4*STEPS_PER_REV);
  }

  // (2) Do homing procedure
  // Serial.println("Starting homing");
  digitalWrite(dirPin, LOW);                                      // Set direction towards the limit switch
  digitalWrite(enPin, HIGH);                                      // Enable motor
  while (digitalRead(limPin) == HIGH && stepsMoved < maxSteps) {  // Move until the limit switch is pressed or timeout
      digitalWrite(stepPin, LOW);
      delayMicroseconds(PULSEWIDTH);  // Adjust this delay to control speed
      digitalWrite(stepPin, HIGH);
      delayMicroseconds(PULSEWIDTH);
      stepsMoved++;
      stepCount--;
  }

  digitalWrite(enPin, LOW);  // Disable motor once homed or timeout (no locking)

  Serial.println(stepsMoved);
  if (stepsMoved >= maxSteps) {
    Serial.println("Homing failed: Timeout reached");
    return false;
  } else {
    stepCount = 0;  // Reset the step count after successful homing
    // Serial.print("Homing successful.");
    // Serial.print("  Steps Moved: ");
    // Serial.println(stepsMoved);
    return true;
  }
}



/**
 * Rotates the stepper motor a specified number of revolutions.
 *
 * This function controls the direction and steps of a stepper motor based on the input
 * revolutions. Positive values will rotate the motor clockwise, while negative values will
 * rotate it counter-clockwise. The motor is enabled before rotation and disabled afterward.
 *
 * @param pulseCount  The number of pulses to send to the motor. Rotates pulseCount*STEPS_PER_REV revolutions
 *                    Use a positive float for clockwise rotation and a negative 
 *                    float for counter-clockwise rotation.
 */
void rotateMotor(long pulseCount) {
  if (abs(pulseCount) > 75 * STEPS_PER_REV)
    return;

  digitalWrite(enPin, HIGH);
  delay(500);

  int dir = 1;
  // Determine direction and total steps
  if (pulseCount > 0) {
    digitalWrite(dirPin, HIGH);  // Clockwise
    dir = 1;
  } else {
    digitalWrite(dirPin, LOW);  // Counter-clockwise
    dir = -1;
  }

  int totalSteps = abs(pulseCount);

  for (int x = 0; x < totalSteps; x++) {
    digitalWrite(stepPin, LOW);
    delayMicroseconds(PULSEWIDTH);  // Adjust this delay to control speed
    digitalWrite(stepPin, HIGH);
    delayMicroseconds(PULSEWIDTH);

    stepCount += dir;  //Keep a running count of the steps
  }

  digitalWrite(enPin, LOW);  //Cut current to motor (no locking)
}

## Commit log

2024-11-06 Create README.md
    Add stepper motor driver documentation
2024-11-06 All arduino methods have callbacks, act as blocking and have timeout functionality
2024-11-08 AISHLoader load/unload sample procedures work without error, sample bed loading also works, homing in progress
2024-11-12 Update README.md: added wiring diagram
2024-11-14 Calibrated ender3 first row loading
2024-11-19 Added ender3 and arduino manual control callbacks
2024-11-21 Add .gitignore for Python bytecode and virtual environments; create ArduinoHardwareTest.py script
2024-11-21 Update .gitignore to include ArduinoHardwareTest.py; remove obsolete ArduinoHardwareTest.py script
2024-11-26 Update .gitignore to include AdaptiveXRD; modify AISH_utils.py for logging; adjust Ender3.py sample positions; refactor app.py for improved hardware connection handling and testing mode
2024-12-02 Implement XRDExperiment class and enhance AISHLoader and AISHExperiment functionality; update app.js for temperature control and procedure time estimation
2024-12-04 updated arduino codes, implemented first version of frontend queuing
2024-12-09 added sample position calibration scripts
2024-12-10 Loading calibrated
2024-12-20 updated BOM
    [AISH BOM.xlsx]
2024-12-20 Added CAD
    [1272T361_Multipurpose 304 Stainless Steel Rod.SLDPRT, 2020 Endcap.SLDPRT, 2020 profile.SLDPRT, 2020-2 profile.SLDPRT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]
